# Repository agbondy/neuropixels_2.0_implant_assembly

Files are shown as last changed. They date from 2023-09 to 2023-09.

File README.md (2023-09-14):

CAD files for a chronic implant assembly for test-phase Neuropixels 2.0 probes in rodents. The design is closely based on the design for the 1.0 implant assembly described and validated in [Luo*, Bondy* et al](https://elifesciences.org/articles/59716) 
with print files available at [this repo](https://github.com/Brody-Lab/chronic_neuropixels).

The assembly consists of four discrete parts: (1) a [dovetail adapter](https://www.janelia.org/open-science/neuropixels-probe-mounts-10-prototype-10-production-and-20-production-versions) permanently glued to the probe base (designed by Wade Sun and the Harris lab at Janelia); (2) an [internal holder](internal%20holder%2065um.stl) that mates with the dovetail adapter and allowed stereotaxic manipulation of the probe; (3-4) an external chassis, printed in two separated parts [here](external%20chassis.stl) and [here](external%20top.stl), that encases and protects the entire assembly. The external chassis and internal holder are attached using screws that can be removed at the end of the experiment to allow explantation and reuse. The dimensions of the 2.0 assembly are significantly smaller than the 1.0 assembly on which it is based, primarily because of the smaller size of the probe and headstage. The maximum dimensions are 24.7 mm (height), 12.2 mm (width), and 11.2 mm (depth), with a weight of 1.5g (not including the headstage). This size and weight make the assembly suitable for chronic implantation in both mice and rats. 

The part files linked above (with the exception of the dovetail adapter) were exported from the parent [.ipt (Inventor) file](neuropixels%202.0%20implant%20assembly.ipt). We also provide a [.form file](all_parts.form) that can be directly printed on Formlabs 3D printers.

The link above associated with the dovetail adapter also contains video instructions for mounting it to a probe.

Note: Dimensions have been tested exclusively using a Form 3 printer, with Black V4 resin and the finest resolution (25um). 
Dimensions will likely need to be adjusted if printed using another method. 
In particular, the parameter "dovetail_gap" in the Inventor file (.ipt) is highly sensitive, and determines how well the probe dovetail mates with the holder. 
This has been highly optimized not just for the print settings listed above, but also the angle of the part in the print file. 
For best results, use the .form file instead of laying the parts out yourself using the CAD files.
The .form file included in the repo prints 5x each part, using the 65um gap version of the internal holder.
The .stl files are exports of the individual parts in the .ipt file.

### Assembling the implant once the parts are printed
See this excellent [assembly instruction manual](https://docs.google.com/document/d/1IJHo09xTRHtCSInflJ-By5AF2hARtQX3Hh1mwAKbEYk/edit?usp=sharing) written by Sarah Jo Venditto.

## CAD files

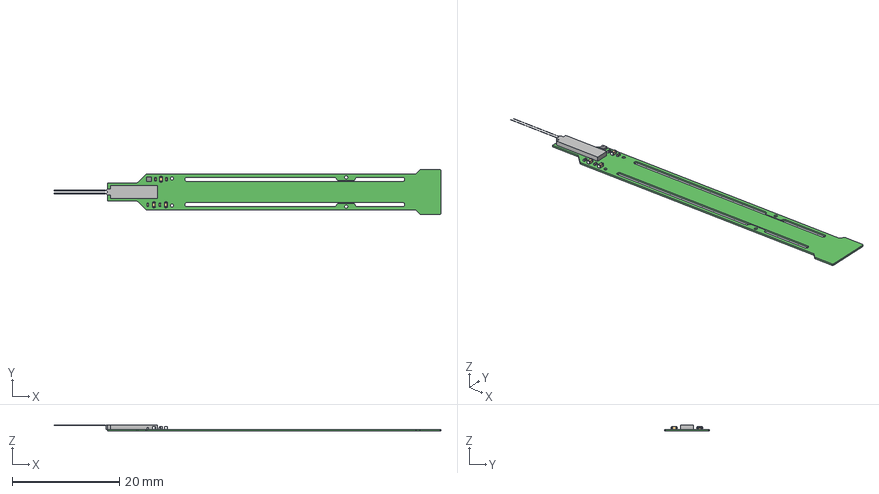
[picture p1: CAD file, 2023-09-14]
IMEC design files/NPM_FLEX_00-00.step
72.2 x 8.40 x 1.10 mm
Board
CerCap_0402 x 3
Extruded x 5
CerCap_0201 x 4

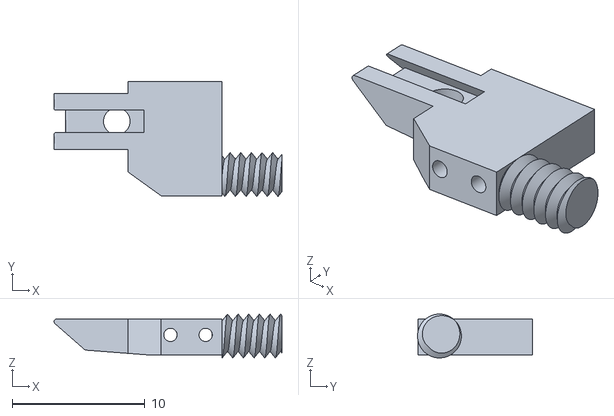
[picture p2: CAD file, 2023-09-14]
internal holder 78um.stl
17.2 x 8.65 x 3.30

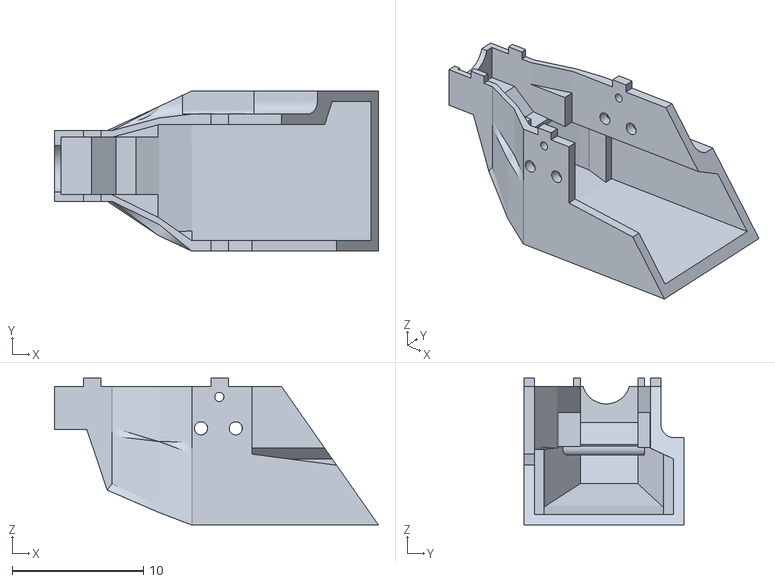
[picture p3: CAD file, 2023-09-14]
external chassis.stl
24.7 x 12.2 x 11.2

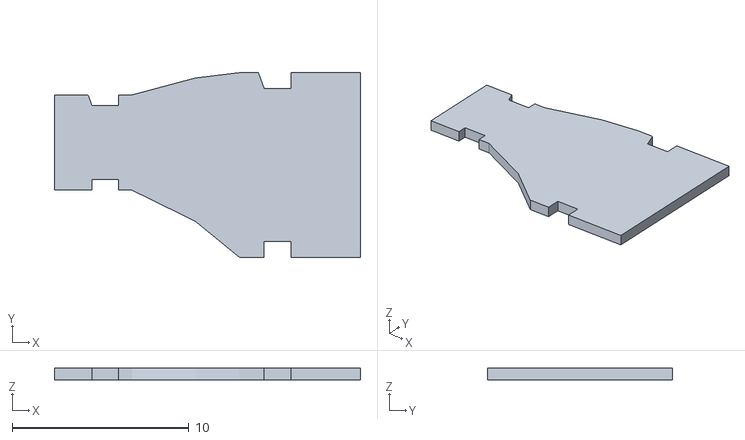
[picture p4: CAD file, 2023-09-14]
external top.stl
17.3 x 10.4 x 0.65

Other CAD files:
internal holder 65um.stl

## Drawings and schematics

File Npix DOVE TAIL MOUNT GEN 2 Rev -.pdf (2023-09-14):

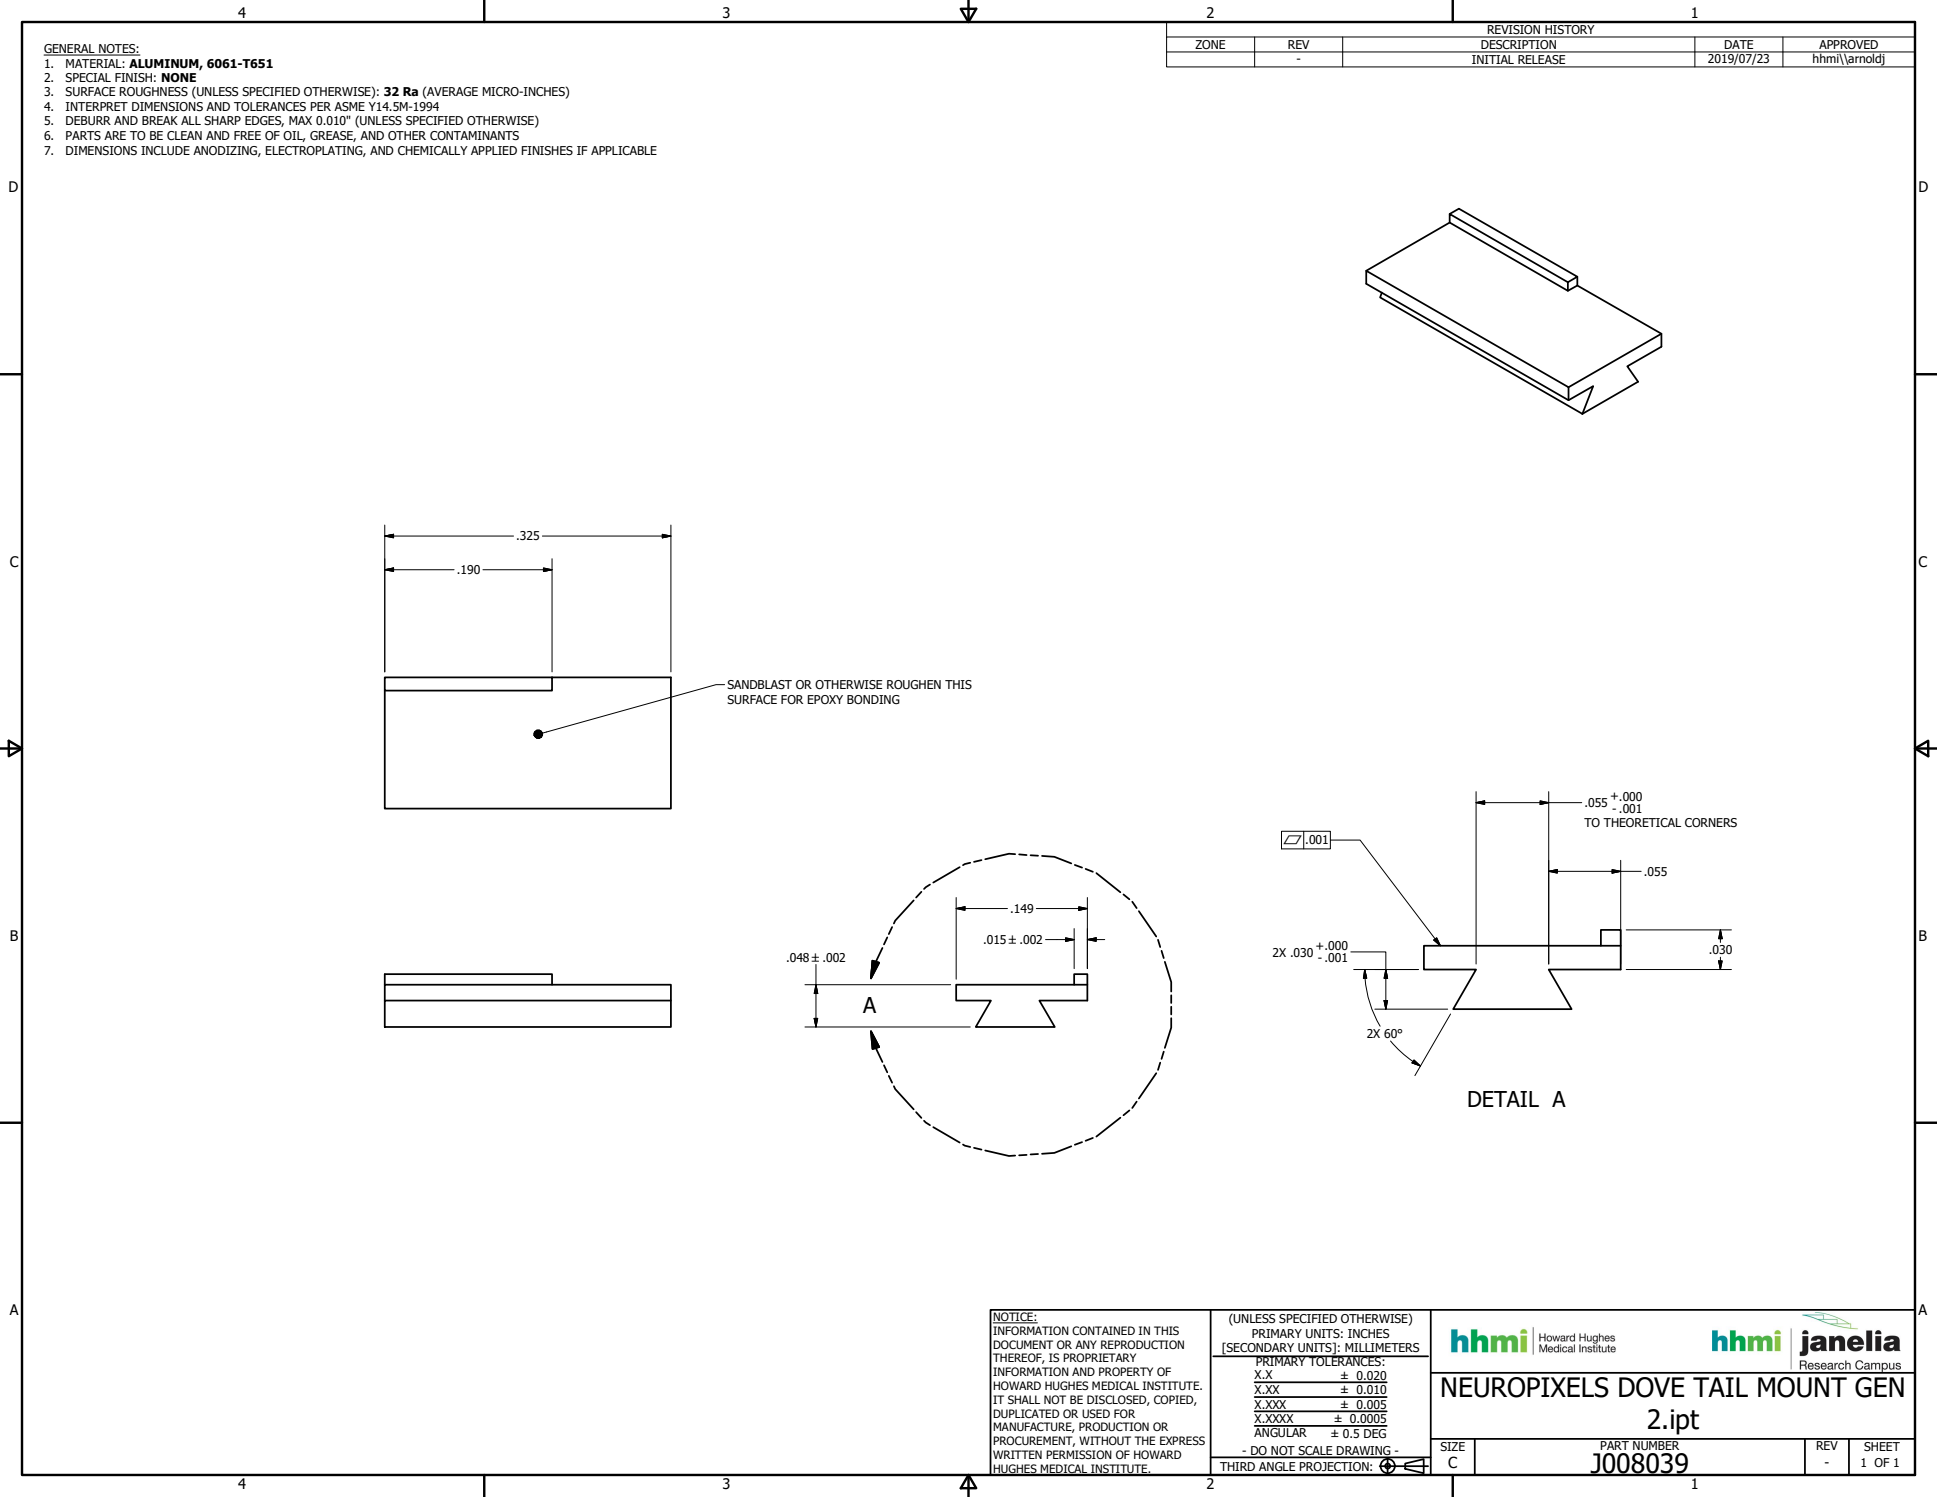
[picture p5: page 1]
DETAIL A; PART NUMBER; 1 OF 1 THIRD ANGLE PROJECTION:; ± 0.020 ± 0.010 ± 0.005 ± 0.0005 ± 0.5 DEG; REVISION HISTORY; - .001 TO THEORETICAL CORNERS

GENERAL NOTES:
1. MATERIAL: ALUMINUM, 6061-T651
2. SPECIAL FINISH: NONE
3. SURFACE ROUGHNESS (UNLESS SPECIFIED OTHERWISE): 32 Ra (AVERAGE MICRO-INCHES)
4. INTERPRET DIMENSIONS AND TOLERANCES PER ASME Y14.5M-1994
5. DEBURR AND BREAK ALL SHARP EDGES, MAX 0.010" (UNLESS SPECIFIED OTHERWISE)
6. PARTS ARE TO BE CLEAN AND FREE OF OIL, GREASE, AND OTHER CONTAMINANTS
7. DIMENSIONS INCLUDE ANODIZING, ELECTROPLATING, AND CHEMICALLY APPLIED FINISHES IF APPLICABLE

ZONE | REV | DESCRIPTION | DATE | APPROVED

- | INITIAL RELEASE | 2019/07/23 | hhmi\\arnoldj

SANDBLAST OR OTHERWISE ROUGHEN THIS
SURFACE FOR EPOXY BONDING

NOTICE:
INFORMATION CONTAINED IN THIS
DOCUMENT OR ANY REPRODUCTION
THEREOF, IS PROPRIETARY
INFORMATION AND PROPERTY OF
HOWARD HUGHES MEDICAL INSTITUTE.
IT SHALL NOT BE DISCLOSED, COPIED,
DUPLICATED OR USED FOR
MANUFACTURE, PRODUCTION OR
PROCUREMENT, WITHOUT THE EXPRESS
WRITTEN PERMISSION OF HOWARD
HUGHES MEDICAL INSTITUTE.

(UNLESS SPECIFIED OTHERWISE)
PRIMARY UNITS: INCHES
[SECONDARY UNITS]: MILLIMETERS
PRIMARY TOLERANCES:
X.XXX
X.XXXX
ANGULAR
- DO NOT SCALE DRAWING -

NEUROPIXELS DOVE TAIL MOUNT GEN
